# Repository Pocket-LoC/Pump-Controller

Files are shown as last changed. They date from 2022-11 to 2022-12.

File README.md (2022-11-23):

# Pocket LoC
 
Lab-on-chip (LoC) technology is becoming increasingly relevant, especially in the field of medicine. However, often LoC setups rely on complex lab equipment for operation. The aim of this project is to create an affordable and portable LoC setup as a proof-of-concept for truly pocket-sized LoC - the Pocket LoC.

Pocket LoC can be assembled with standard equipment found in a typcial engineering lab (such as a maker space or FabLab). Once assembled, Pocket LoC is fully portable and only needs a PC to operate.

## Pump Controller
 

The pump controller for the Pocket LoC is designed as an interface for the [Bartels mp-Highdriver4](https://www.bartels-mikrotechnik.de/en/microelectronics/) and uses a microcontroller (Atmel ATmega32U4). The sensor can be operated like an Arduino with connected peripherals, making coding simple.

The mp-Highdriver4 and four micropumps (mp6-liq) can be plugged directly into the controller to achieve a compact form factor.

### Components

Prices are estimates of current prices:
- PCB 25-50€ (depends on manufacturer)
- Circuit components (see Altium project for details) approx. 25€
- [Bartels mp-Highdriver4](https://darwin-microfluidics.com/products/mp-highdriver4-pump-driver?variant=39540556791972) 159€
- 4x [Bartels mp6-liq](https://darwin-microfluidics.com/products/bartels-mp6-micropump?variant=36928480837796) 128€

### PCB assembly

All design files for the PCB can be found as an Altium project in the [hardware folder](https://github.com/Pocket-LoC/Pump-Controller/tree/main/Hardware). You can order the ready printed PCB from manufacturers like [JLCPCB](https://jlcpcb.com/) or [multi-cb](https://www.multi-circuit-boards.eu/en/index.html) and assemble it yourself (requires tools and skills for SMD assembly), order an assembled PCB or contact me.

Once assembled, the microcontroller will have to be initially flashed with a bootloader (requires an ISP device, e.g. an Arduino) and then can be programmed and used via a regular USB connection. Details on flashing the bootloader and firmware usage can be found [here](https://github.com/Pocket-LoC/Pump-Controller/tree/main/Firmware).

### Device assembly

When assembling the pump driver section, ensure that the marked "PIN1" on the driver section (Bartels mp-Highdriver4) is aligned with the USB connector of the controller. Then insert the micropumps (Bartels mp6-liq), ensuring that the arrows are facing away from the USB connector, and close the connectors by pushing them down. Tweezers may help if you have to open the connectors again to remove the pumps.

<p float="left">
        
         
        
        
</p>

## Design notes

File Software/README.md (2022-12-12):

## Pocket LoC Pump Controller

### Sample Software
This is a software sample to help you getting started with the controller firmware. The sample uses Python to establish a serial connection, configure the controller parameters and run a sample droplet program.

#### Getting Started
To run this code you will need to install Python (3.7+). Typically, it is easiest to use an IDE such as Spyder or Visual Studio. Depending on your setup you may have to install some of the used packages (see "import" statements at the top of the file or just run and wait for errors). Packages are usually installed using pip or conda, depending on your installation.

Connect the Pocket LoC Pump Controller (with the [firmware](https://github.com/Pocket-LoC/Pump-Controller/tree/main/Firmware) loaded and four micropumps connected). The blue LED should be on.

You can now run the Python code. The software will try to establish a connection to the first "Arduino Micro" that identifies as Pocket LoC pump controller. It will then configure the controller and wait for input confirmation to start the droplet sample. The sample assumes that pump 1 provides a constant background flow and pumps 2 through 4 are used to generate droplets. You will have to adjust the droplet timings and voltages for your specific application.

### Bartels Multiboard App
For a quick and simple test and operation of the pumps, you can use this applet provided by the pump manufacturer. Select the correct serial port (can be found in the systemd device manager) and the "Highdriver4". You can now set the driver frequency and control the individual pump voltages.

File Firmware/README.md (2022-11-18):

## Pocket LoC Pump-Controller

### Firmware
This is the firmware for the Pocket LoC pump controller. As the controller uses an ATmega32U4 microcontroller, we can use it like an Arduino Micro. To use this firmware install the [Arduino IDE](https://www.arduino.cc/en/software).

#### Flashing the bootloader
Before we can use the controller via the USB connection, we have to flash it with a bootloader. This can be easily done from the Arduino IDE using either a different [Arduino](https://docs.arduino.cc/built-in-examples/arduino-isp/ArduinoISP#the-bootloader) or a dedicated [ISP](https://docs.arduino.cc/hacking/software/Bootloader#burning-the-bootloader) device. Remember to select "Arduino Micro" as a target. The controller has a compact [Tag-Connect](https://www.tag-connect.com/product/tc2030-idc-nl-10-6-pin-plug-of-nails-spring-pin-cable-with-0-1-ribbon-connector-10-version) ISP header - see below for the pinout. All other necessary information can be found in the linked manuals.



#### Using the Firmware
Clone this repository and open the .ino file in the Arduino IDE. Connect the pump controller with a USB cable (micro USB-B), select the correct port in the IDE (the sensor will appear as "Arduino Micro"), and upload the sketch. That will take a few moments and the LEDs will flash.

Finally, you are ready to go! You can now use the controller as a serial device (do not forget to connect the Bartels Highdriver-4). Here is a list of commands you can send (each command must be terminated with "\r\n"):

- P\<x>V\<yyy>

  Set the voltage of pump <x> to <yyy>. The voltage is proportional to the pump output and can be in the range of 0V to 250V.
  
- P\<x>ON

  Activate pump \<x>. Voltage and frequency will be applied depending on the current settings.
 
- P\<x>OFF

  Deactivate pump \<x>. This will not reset the voltage setting.
  
- PA\<aaa>#\<bbb>#\<ccc>#\<ddd>

  Set the voltage of all four pumps (\<aaa> for pump 1, \<bbb> for pump 2, ...). Each value must be zero-padded to exactly three characters.
  
- PON

  Activate all pumps (i.e. apply voltage set previously).
  
- POFF

  Deactivate all pumps.
  
- SELECTQUADDRIVER

  Setup the controller to use the Bartels Highdriver-4. This should be called during initialisation.

#### Getting Started
You can use the "serial monitor" in the Arduino IDE to quickly test the controller with some first commands. Make sure you select carriage return and newline as command terminators. In the [software folder](https://github.com/Pocket-LoC/Pump-Controller/tree/main/Software) you will find a Python example to configure the controller and run a sample droplet program.

#### General Information

- The controller has a blue LED that indicates it is powered.
- A red LED is connected to PD7 (Arduino 27) and is active high.
- Both settable I2C-Adress pins on the Highdriver-4 are bound to high (Adress: 0x7b).

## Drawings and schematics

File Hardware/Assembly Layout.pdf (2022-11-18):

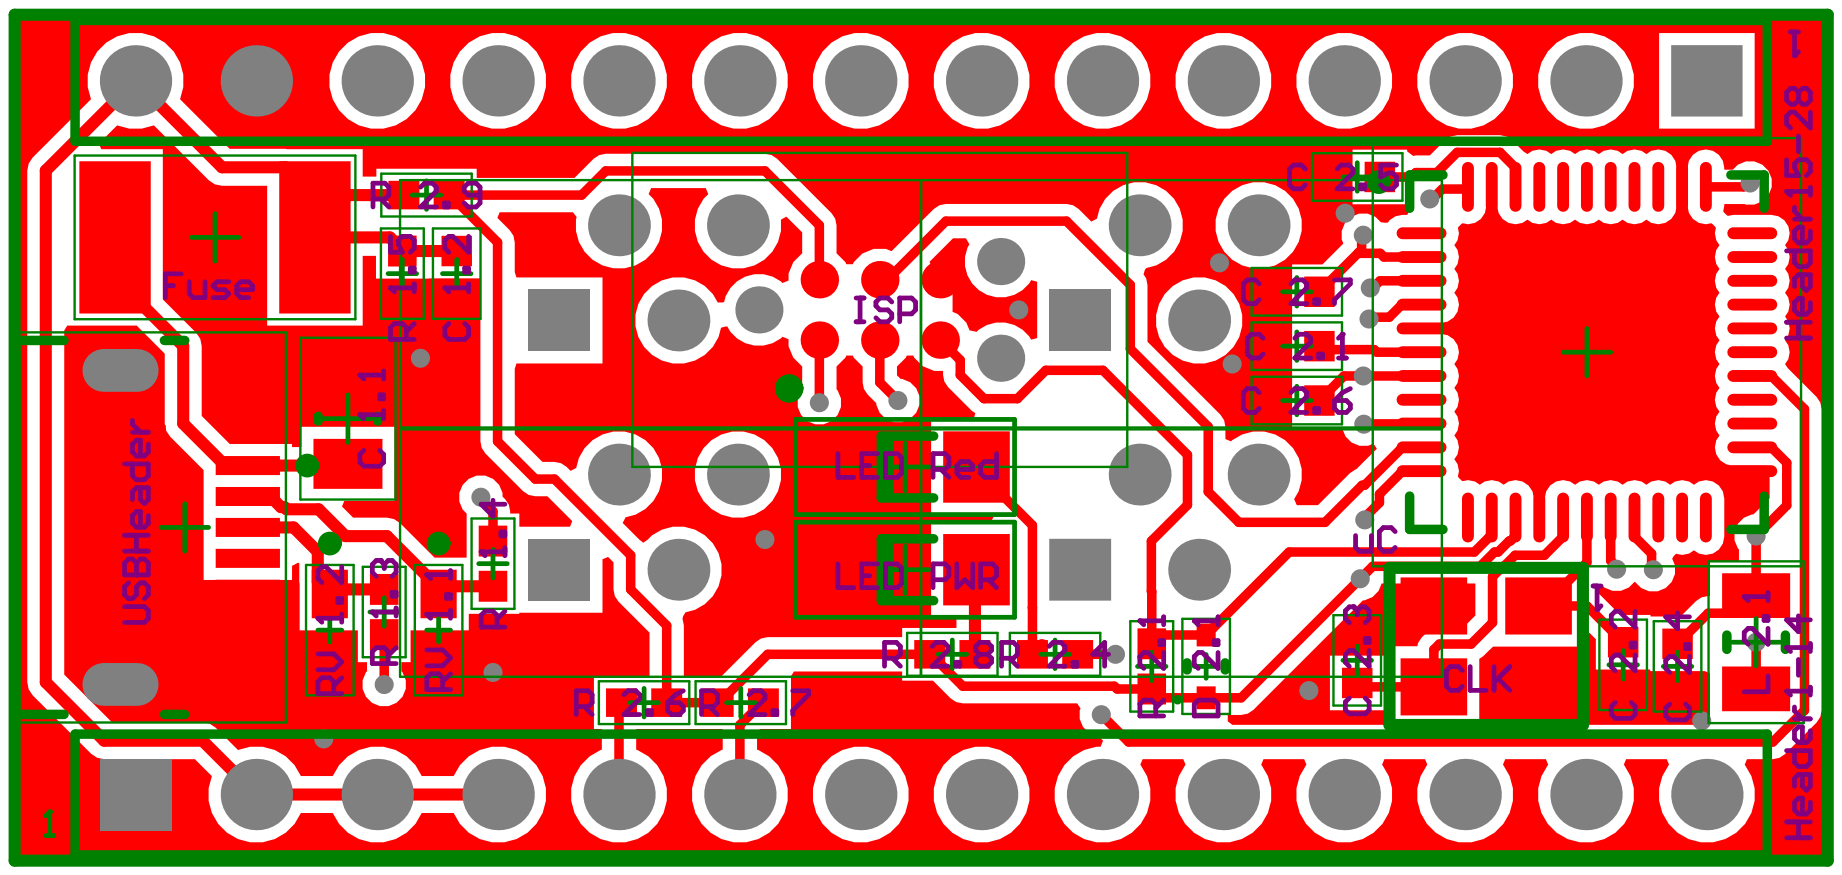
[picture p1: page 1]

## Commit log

2022-11-18 Add base files
    [7M-16.000MAAE-T.PcbLib, 7M-16.000MAAE-T.SchLib, ATMega32U4.SchDoc, BartelsInterface.PrjPcb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]
2022-11-18 Create Sample Pump Control.py
